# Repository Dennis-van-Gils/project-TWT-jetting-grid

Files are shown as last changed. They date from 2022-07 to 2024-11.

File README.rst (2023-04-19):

*This repository involves the Jetting Grid of the Twente Water Tunnel (TWT) facility of the University of Twente, Physics of Fluids group.*

Introduction
============

The Jetting Grid is essentially a turbulence generator. It consists of a rectangular array of 112 individually computer-controlled water jets that are aligned streamwise to the measurement section of our 8 meter tall vertically recirculating water tunnel. Individual jets will turn on and off following predefined 'protocols' tailored to different turbulent statistics inside the measurement section. The protocols are based on 4-dimensional OpenSimplex
noise: a type of gradient noise that features temporal and spatial coherence.

..
  More details can be found in the Review of Scientific Instruments article found here.

In this repository you can find:

.. list-table::
  :widths: 50 50

  * - The electronic design diagram
    - `</docs/electronic_diagram.pdf>`_
  * - The electronics cabinet in 3D-CAD
    - `</Solidworks/_main_cabinet.pdf>`_
  * - The microcontroller C++ source code and firmware
    - `</src_mcu>`_
  * - The Python user control program
    - `</src_python>`_
  * - The protocol generator based on 4D-OpenSimplex noise
    - `</protocols>`_
  * - Project photos
    - `</docs/photos>`_

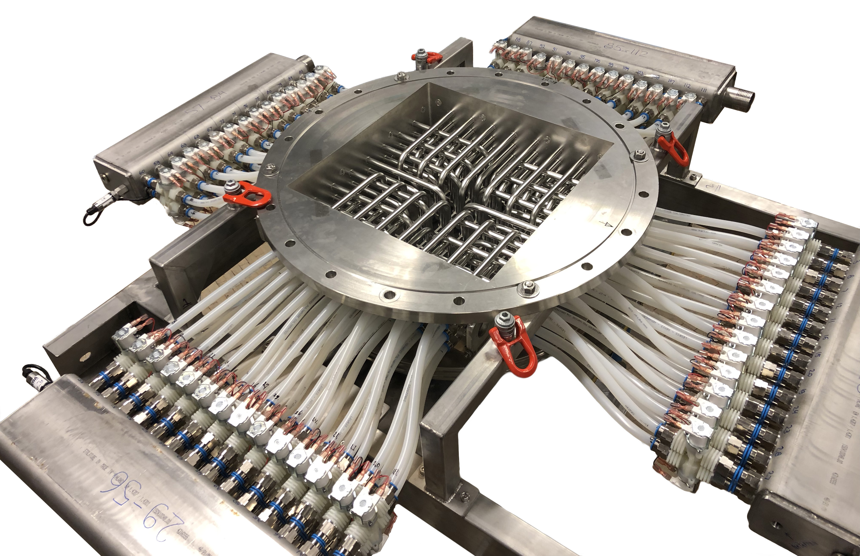
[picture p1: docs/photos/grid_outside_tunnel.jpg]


  *Figure 1: The jetting grid before installation in the tunnel.*

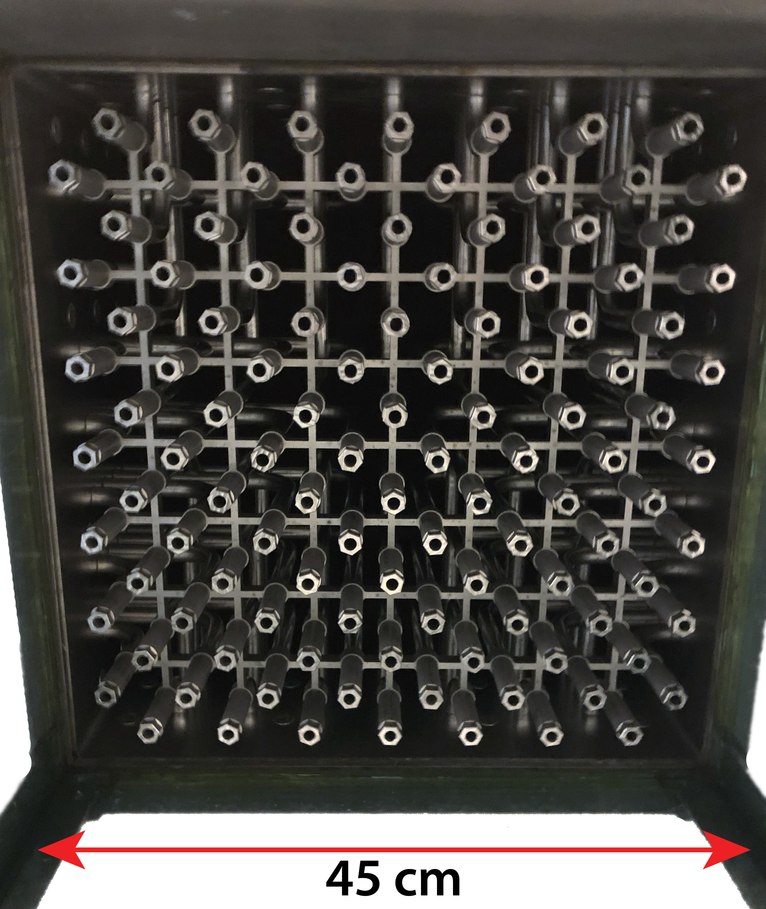
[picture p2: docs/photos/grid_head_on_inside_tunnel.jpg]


  *Figure 2: The jetting grid inside of the tunnel viewed head-on through the measurement section of cross-section 0.45 m by 0.45 m.*

Extended introduction
=====================

All jetting nozzles are powered by a single water pump providing the driving pressure for the jets. Each nozzle is controlled by an individual solenoid valve that can be programmatically opened or closed. The valves of the grid come in through the 4 side walls of the tunnel section with 28 valves through each side: 4 x 28 = 112 valves. Each set of these 28 valves shares a common pressure distribution manifold of which we will monitor the pressure.

An Arduino controls the 112 solenoid valves, reads out the 4 pressure sensors and drives a 16x16 LED matrix to visualize the status of each valve.

Protocol coordinate system (PCS)
================================

The jetting nozzles are laid out in a square grid, aka the protocol coordinate system (PCS): ::

      ●: Indicates a valve & nozzle
      -: Indicates no nozzle & valve exists

         -7 -6 -5 -4 -3 -2 -1  0  1  2  3  4  5  6  7
        ┌─────────────────────────────────────────────┐
      7 │ -  ●  -  ●  -  ●  -  ●  -  ●  -  ●  -  ●  - │
      6 │ ●  -  ●  -  ●  -  ●  -  ●  -  ●  -  ●  -  ● │
      5 │ -  ●  -  ●  -  ●  -  ●  -  ●  -  ●  -  ●  - │
      4 │ ●  -  ●  -  ●  -  ●  -  ●  -  ●  -  ●  -  ● │
      3 │ -  ●  -  ●  -  ●  -  ●  -  ●  -  ●  -  ●  - │
      2 │ ●  -  ●  -  ●  -  ●  -  ●  -  ●  -  ●  -  ● │
      1 │ -  ●  -  ●  -  ●  -  ●  -  ●  -  ●  -  ●  - │
      0 │ ●  -  ●  -  ●  -  ●  -  ●  -  ●  -  ●  -  ● │
     -1 │ -  ●  -  ●  -  ●  -  ●  -  ●  -  ●  -  ●  - │
     -2 │ ●  -  ●  -  ●  -  ●  -  ●  -  ●  -  ●  -  ● │
     -3 │ -  ●  -  ●  -  ●  -  ●  -  ●  -  ●  -  ●  - │
     -4 │ ●  -  ●  -  ●  -  ●  -  ●  -  ●  -  ●  -  ● │
     -5 │ -  ●  -  ●  -  ●  -  ●  -  ●  -  ●  -  ●  - │
     -6 │ ●  -  ●  -  ●  -  ●  -  ●  -  ●  -  ●  -  ● │
     -7 │ -  ●  -  ●  -  ●  -  ●  -  ●  -  ●  -  ●  - │
        └─────────────────────────────────────────────┘

The PCS spans ``(-7, -7)`` to ``(7, 7)`` where ``(0, 0)`` is the center of the grid. Physical valves are numbered 1 to 112, see `/docs/jetting_grid_indices.pdf </docs/jetting_grid_indices.pdf>`_.

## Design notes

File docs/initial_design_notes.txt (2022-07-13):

Solenoid water valve
--------------------

Number of valves:
Decided: 112, 28 per side, pref 12 mm inner diam

Typical 24V water solenoid valve draws 250 mA

Requirements solenoid valve:
- operate at 24 V (preferably: keep the current below 290 mA for the PVT312 solid state relay)
- diameter ~ 10 mm, 1/2", 3/8"
- fast acting ~ 0.5 to 1 sec
- direct or indirect (requires P_diff) controlled

Circuitry
---------

Use Arduino + Millipede board (MCP23017, 16 ch, I2C) + MOSFET board
Add a square matrix LED panel for jet visualisation.

Centipede: 64 channels extra DIO from I2C
Can probably take in 3.3 V I2C

  MOSFETS
  -------

Google: https://www.google.com/search?q=mosfet+board+16+channels&client=firefox-b-d&biw=1509&bih=934&sxsrf=AOaemvJO6wwmgFGnOk4NJ1rpOsNPfvxfmA:1638218075573&tbm=isch&source=iu&ictx=1&fir=AU-XXLih75zALM%252CS97yPO1Kx7uSEM%252C_%253B9pQUPeZW437mgM%252CEUD3R4LZVhkzxM%252C_%253Bhjt8wuJb8bHoEM%252CFV8Iuv8lZduGGM%252C_%253BljEDhoefagN5KM%252Cti9fFwPpx9osCM%252C_%253BCxuMXcBo8yG1DM%252CEUD3R4LZVhkzxM%252C_%253Be8bhNiFRVqvsCM%252CFV8Iuv8lZduGGM%252C_%253BFx3XZ33hJDuYoM%252CSX-uN8D8Pt4YaM%252C_%253BxeoLwY-jtr72NM%252CGLllsm-Hn3OM_M%252C_%253BPi-L7esW3UOClM%252CdukqlienmSXj_M%252C_%253B2DBUNCfDyTJj9M%252CGLllsm-Hn3OM_M%252C_&vet=1&usg=AI4_-kRFkAliVR6oQi8AF89qi7QxvJARFg&sa=X&ved=2ahUKEwioxNXztb70AhXdh_0HHbOiAd8Q9QF6BAgDEAE#imgrc=TQaBvuL1G480wM
  
Perhaps go with mosfets instead of solid state relays.
background: https://www.omron-ap.com/service_support/FAQ/FAQ02243/index.asp
not sold anymore: https://nl.aliexpress.com/item/295106416.html
good, but discontinued https://www.seeedstudio.com/16-Ch-High-Current-Driver-Shield-Kit-v2-p-793.html

Candidates MOSFET boards:
  1)  http://www.icstation.com/channel-amplifier-module-isolated-transistor-controller-signal-converter-16bit-protector-optocoupler-p-14065.html
      https://www.joom.com/en/products/5ee21e888b45130101fa9668
      https://nl.aliexpress.com/item/32802013615.html?spm=a2g0o.productlist.0.0.1ad72fd72K1Lzm&algo_pvid=5d4b663b-750f-42e6-8c23-180898b16d44&algo_exp_id=5d4b663b-750f-42e6-8c23-180898b16d44-46&pdp_ext_f=%7B%22sku_id%22%3A%2264206637981%22%7D
      
      Brand: Sanwo
      specs: optocoupled, < 1 ms response, 1 kHz switching freq, with LED indicators
             NPN in, NPN out
      eur 32

  2)  https://de.aliexpress.com/item/33014054266.html
      http://en.ginri.com/products-id60.html
      https://nl.aliexpress.com/item/32838587215.html?spm=a2g0o.productlist.0.0.21df7e0bMamRsn&algo_pvid=8064bbcf-e388-47e7-9a27-8b6d5d5a820e&algo_exp_id=8064bbcf-e388-47e7-9a27-8b6d5d5a820e-31&pdp_ext_f=%7B%22sku_id%22%3A%2265134071861%22%7D
      
      Brand: Ginri
      specs: > 5 kHz switching
             NPN or PNP in, PNP out
      eur 46.12

Design
------
Add master mechanical relay to control ENA_relays?
Decision: No. Relays should stay powered as they are to prevent
waterhammer when they would otherwise all close simultaneously in case
of EM stop or MCU restart.

Pumps
-----
Looking for 3-5 bar and 350l/min.

Flow meter ?
---------------
Before intake of pump
Decision: no, we only rely on pressure

Pressure sensor?
-----------------
Perhaps 1 on each manifold?
Decision: yes
Put manual restriction valve before each manifold to tune equal pressure distribution

How many valves will be enabled simultaneously?
-----------------------------------------------
If we choose to open all 112 valves it will draw 112 * 0.265 A = 30 A.
And the power draw will be 30 A * 24 V = 720 W.
This is fairly large. Not impossible, but I have to design for this.

Decision: Design for all valves open simultaneously at once, during measurement just 30

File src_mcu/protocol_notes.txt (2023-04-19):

Protocol file format:
    - Plain ASCII, tab delimited, rows ending with '\n' , not '\n\r'
    - Assume each row all valves are turned off, unless listed 

    [HEADER]
    ... (info to be able to generate the protocol)
    [DATA]
    [duration in ms, max 2^16-1] [list of open valves in grid (-7,-7) to (7,7)]
    50       -7,-2    3,2    1,2    4,-2
    50       -6,-4    3,6    -3,2
    100      ..... 

Memory allocation @ Arduino:

    Protocol:

    Send from Python to Arduino via binary serial stream
    ----------------------------------------------------
    Sends a single protocol line each time as follows:
      1x2 bytes: Duration in ms, big-endian
      Nx1 bytes: Each PCS point (x, y) packed into a single byte.
                 Upper 4 bits = PCS.x, lower 4 bits = PCS.y
      1x3 bytes: End-of-line (EOL) sentinel: [0xFF, 0xFF, 0xFF]

    When received at Arduino side
    -----------------------------
    Each line gets transformed into a 16x16 boolean matrix where all send PCS
    coordinates are 1's, the rest 0.
    Next, we pack each row of the matrix into a 16 bit structure, i.e. uint16_t.
    We have 15 rows of each 16 bits --> 30 bytes for the full boolean matrix
    +2 bytes for the time duration in ms as uint16_t
    ----> 30 + 2 = 32 bytes per protocol line, fixed number of bytes, regardless
    of how many valves should be opened or closed.
    This allows us to define a fixed-size array within C++, yeay!
    Say we have 180.000 bytes of RAM left over to play with:
    --> 180000/32 = 5625 protocol lines will fit into memory.
    Hence, we safely limit the max number of lines a protocol can contain to
    5000.

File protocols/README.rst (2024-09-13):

Protocols
=========

Contains the Python scripts to generate protocols for the jetting grid of the
Twente Water Tunnel facility.

Installation
------------

1) Download the contents of this GitHub folder `here <https://download-directory.github.io/?url=https%3A%2F%2Fgithub.com%2FDennis-van-Gils%2Fproject-TWT-jetting-grid%2Ftree%2Fmain%2Fprotocols>`_ and unzip.
2) Open Anaconda prompt and navigate into the unzipped folder.
3) Now, we will create a separate Python environment called 'twt' to install the necessary packages and run the scripts in.

    In Anaconda prompt::

        conda create -n twt python=3.10
        conda activate twt
        pip install -r requirements.txt

Usage
-----

* Edit ``config_proto_opensimplex.py`` to your needs.
* Set global flags in ``make_proto_opensimplex.py`` to your needs.

In Anaconda prompt::

    conda activate twt
    ipython make_proto_opensimplex.py

Example output
--------------

See the `protocols subfolder </protocols/protocols>`_.


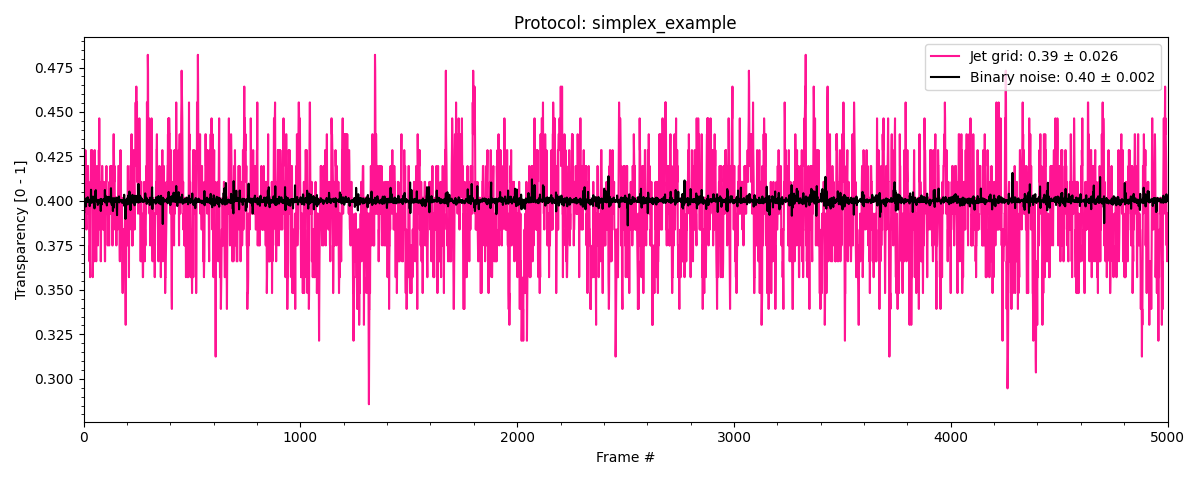
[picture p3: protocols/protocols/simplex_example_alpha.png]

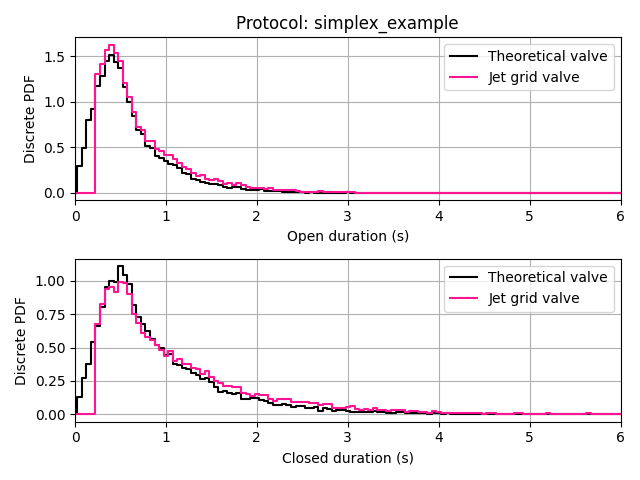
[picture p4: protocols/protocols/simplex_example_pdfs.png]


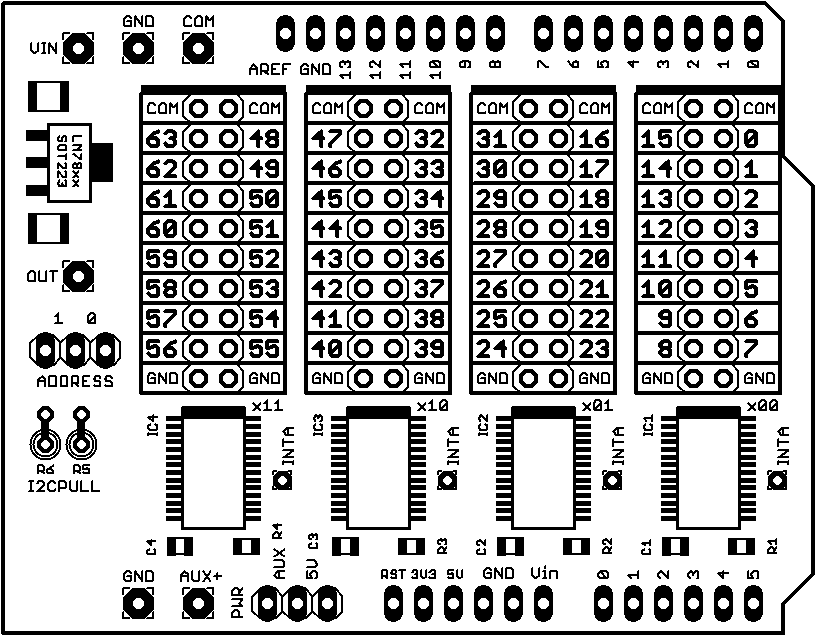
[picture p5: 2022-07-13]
docs/electronics/io_expander_centipede/photos/centipede_bitmap.png

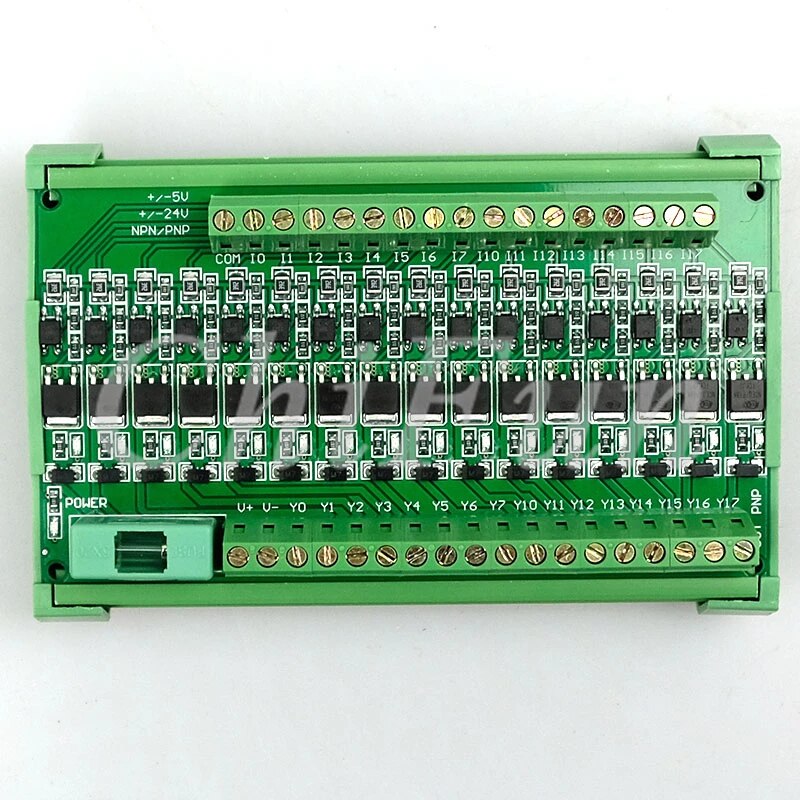
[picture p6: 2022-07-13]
docs/electronics/mosfet_board/photos/16-manier-PLC-versterkerprint-isolatie-boord-bescherming-boord-ingang-NPN-PNP-uitgang-PNP.jpg_Q90.jpg_.jpg

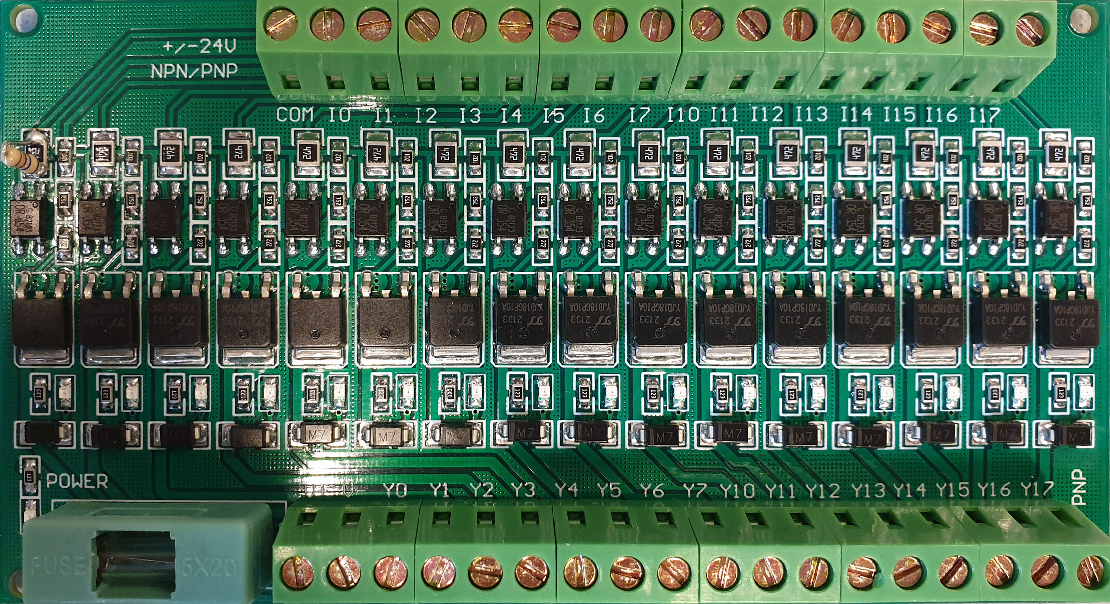
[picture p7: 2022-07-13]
docs/electronics/mosfet_board/photos/Sanwo_mosfet_board.jpg

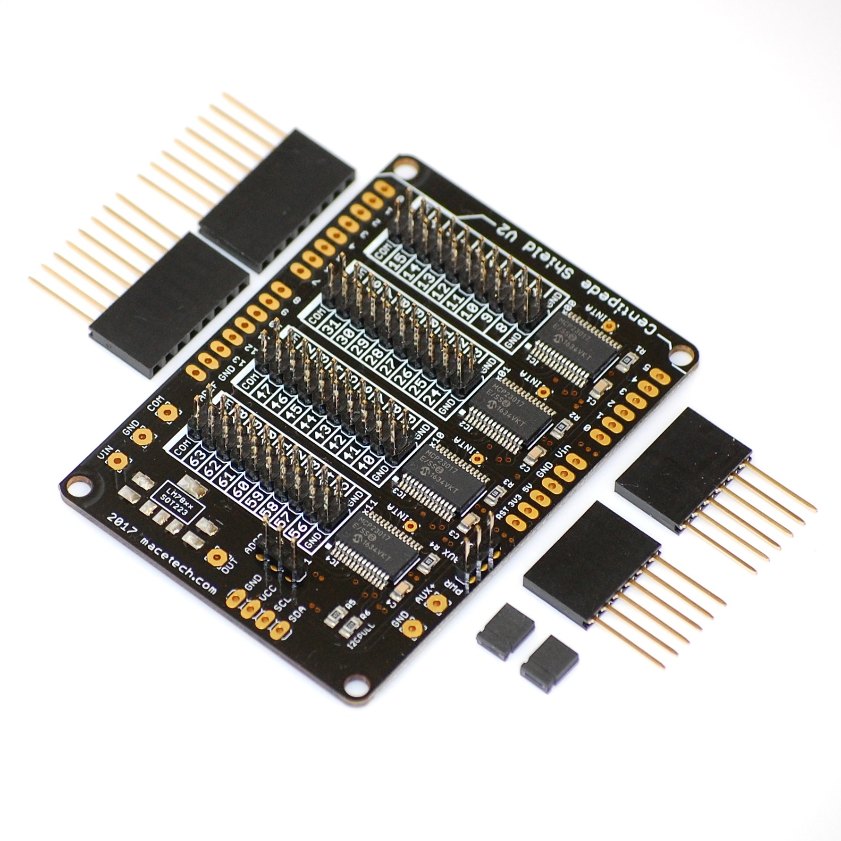
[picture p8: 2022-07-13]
docs/electronics/io_expander_centipede/photos/2019-11-24T07 14 23.657Z-DSC_6497.JPG

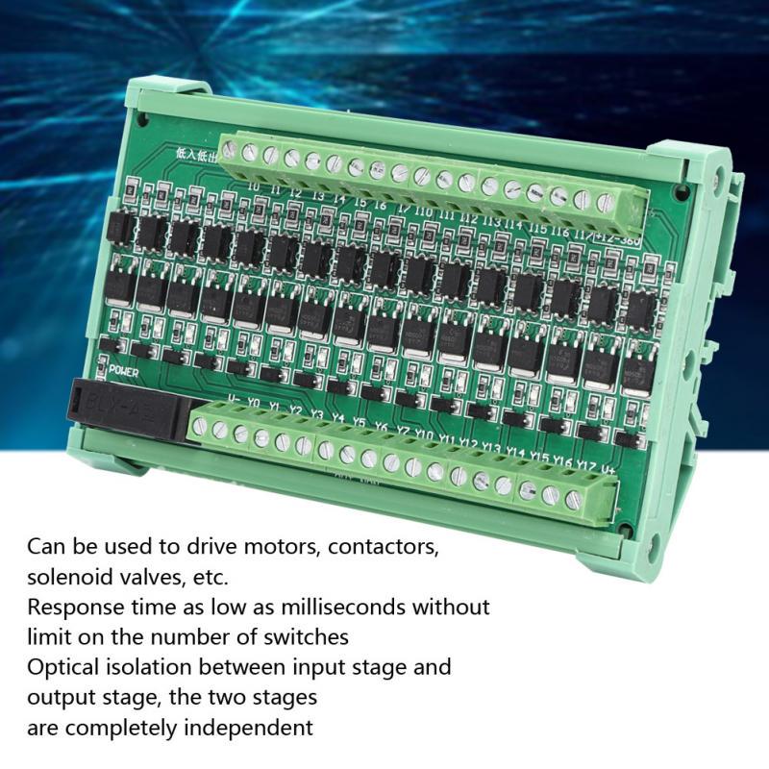
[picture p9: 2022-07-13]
docs/electronics/mosfet_board/photos/Sanwo.jpeg

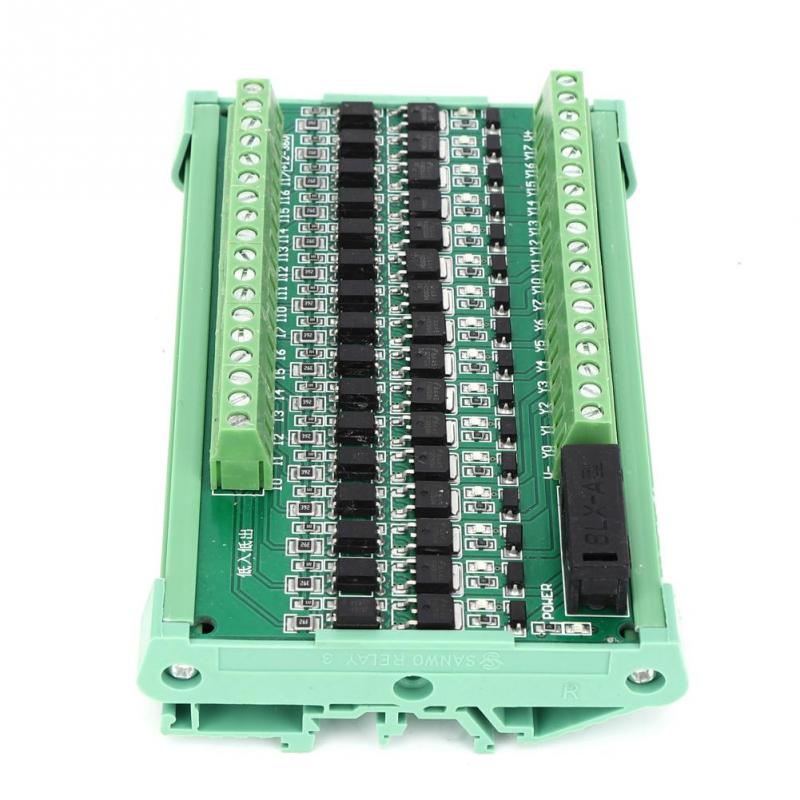
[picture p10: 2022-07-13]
docs/electronics/mosfet_board/photos/6e6c67497c9603db31151731857741b0994e5a79_original.jpeg

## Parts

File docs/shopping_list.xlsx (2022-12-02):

OFI: 30912301, PROJECT: 20001599-10
 | Delivered? | Item | Brand & type | Price per unit | Count | Total price | Link | Specs
Valves | yes | solenoid valves | RPE 5105NC-24VDC | €16.19 | 140 | €2266.60 | https://tameson.nl/kleppen/magneetventiel/2-weg/plastic/5105nc-24vdc-magneetventiel-2weg-012inch-nylon-0p2-10bar-nbr.html | 24 V, 265 mA
Main electronics | yes | Adafruit Feather M4 Express | Adafruit #3857 | €27.50 | 1 | €27.50 | https://www.kiwi-electronics.nl/en/adafruit-feather-m4-express-featuring-atsamd51-3578
 | yes | I2C I/O expander, 64 ch. | Macetech Centipede V2 | €25.00 | 2 | €50.00 | https://shop.macetech.com/products/centipede-shield-v2
 | yes | mosfet board, opto-coupled, 16 ch. | Aliexpress, Sanwo? | €22.22 | 8 | €177.76 | https://nl.aliexpress.com/item/32802013615.html
 | yes | pressure transducer | Omega PXM309-007GI | €137.00 | 4 | €548.00 | https://www.omega.nl/pptst/PXM309.html | G 1/4 (1/4" BSPP)
 | yes | pressure snubber | Omega PS-4E-MG | €14.50 | 4 | €58.00 | https://www.omega.nl/pptst/PS_SNUBBERS.html | G 1/4
 | yes | 4-20 mA receiver | MIKROE-1387 | €20.21 | 4 | €80.84 | https://nl.rs-online.com/web/p/products/8828948/
 | yes | PSU, 24 V, 31 A, 750 W | TRACO POWER TXLN 750-124 | €274.00 | 1 | €274.00 | https://nl.farnell.com/traco-power/txln-750-124/power-supply-ac-dc-24v-31-3a/dp/3647863 | For solenoid valves
 | yes | PSU din rail, 3.3 V, 2.6 A, 8.6 W | CUI PSK-10D-3-DIN | €15.00 | 1 | €15.00 | https://nl.farnell.com/cui/psk-10d-3-din/power-supply-ac-dc-3-3v-1-515a/dp/3702409 | For Arduino
 | yes | PSU din rail, 5 V, 6 A, 30 W | XP POWER DNR30US05 | €33.00 | 1 | €33.00 | https://nl.farnell.com/xp-power/dnr30us05/psu-din-rail-30w-5v/dp/1372693 | For LED matrix
 | yes | LED matrix, NeoPixel 16x16 | Adafruit #2547 | €85.00 | 1 | €85.00 | https://www.digikey.nl/nl/products/detail/adafruit-industries-llc/2547/5777186
 | yes | USB-RS485 isolated adapter | Titan USB-COMi-Si-M | €94.00 | 1 | €94.00 | https://www.antratek.nl/usb-comi-si-m
Safety microcontroller | yes | Adafruit Feather M0 Basic Proto | Adafruit #2772 | €22.72 | 1 | €22.72 | https://nl.rs-online.com/web/p/microcontroller-development-tools/1245520
 | yes | FeatherWing Doubler | Adafruit #2890 | €8.55 | 1 | €8.55 | https://nl.rs-online.com/web/p/breadboards/1245499
 | yes | Non-latching relay for Adafruit Feather | Adafruit #2895 | €9.07 | 1 | €9.07 | https://nl.rs-online.com/web/p/power-motor-robotics-development-tools/1245530
Custom perfboard | yes | perfboard 160x100 mm (set of 4) | Tru Components T1906SA024 | €25.61 | 1 | €25.61 | https://www.conrad.nl/nl/p/tru-components-printplaat-epoxide-l-x-b-160-mm-x-100-mm-35-m-rastermaat-2-54-mm-inhoud-4-stuk-s-2137879.html
 | yes | PCB 160x100 carrier DIN rail | DamenCNC 2340 | €21.00 | 2 | €42.00 | https://www.damencnc.com/en/din-rail-mount-for-eurocard-pcb-100x160mm/a1562
 |  | ↳ cheaper (next time) | Aliexpress |  |  |  | https://nl.aliexpress.com/item/32626843415.html
 | yes | screw terminals 4x, 2.54 pitch | Multicomp MP008515 | €0.82 | 20 | €16.40 | https://nl.farnell.com/multicomp-pro/mp008515/tb-wire-to-brd-r-a-4way-18awg/dp/3817462
 | yes | headers, 1x8 stacking | Multicomp 2212S-08SG-85 | €0.12 | 30 | €3.60 | https://nl.farnell.com/multicomp/2212s-08sg-85/socket-pcb-1-row-8way/dp/1593463
 | yes | DIP socket, 2x7 | Multicomp 2227MC-14-03-10-F1 | €0.22 | 10 | €2.20 | https://nl.farnell.com/multicomp/2227mc-14-03-10-f1/socket-ic-dil-0-3-14way/dp/1103845
Cables & connectors | yes | Han-ECO bulkhead housing | Harting 19 41 024 0301 | €14.00 | 8 | €112.00 | https://nl.farnell.com/harting/19-41-024-0301/housing-bulkhead-han-eco-24b/dp/1892252
 | yes | Han-ECO hood, M40 gland | Harting 19 41 124 0523 | €35.00 | 8 | €280.00 | https://nl.farnell.com/harting/19-41-124-0523/hood-s-e-m40-han-eco-24b-with/dp/1892257
 | yes | Han E screw module F | Harting 09 14 005 2701 | €7.40 | 56 | €414.40 | https://nl.farnell.com/harting/09-14-005-2701/rectangular-insert-signal-rcpt/dp/2382689
 | yes | Han E screw module M | Harting 09 14 005 2601 | €10.70 | 56 | €599.20 | https://nl.farnell.com/harting/09-14-005-2601/rectangular-insert-signal-plug/dp/2382688
 | yes | cable 35 x 0.5 mm2, per 50 meter | ÖLFLEX CLASSIC 110, 1119035 | €243.80 | 1 | €243.80 | https://www.conrad.nl/p/lapp-olflex-classic-110-stuurstroomkabel-35-g-050-mm-grijs-1119035-50-50-m-1029944 | OD 14.5 mm
 | yes | USB panel mount | TRU COMPONENTS USB-08 1243946 | €15.00 | 1 | €15.00 | https://www.conrad.nl/p/usb-inbouwbus-30-usb-08-1243946-tru-components-1-stuks-1243946
 | yes | ribbon cable, 2x10 header, 60 cm | Amphenol FC20600-0 | €2.34 | 10 | €23.40 | https://nl.farnell.com/amphenol/fc20600-0/lead-2-54mm-f-f-600mm-20way/dp/2217640
 | yes | ribbon cable, 20 way, 24 AWG, 25 m | Pro power PP001506 | €49.14 | 1 | €49.14 | https://nl.farnell.com/pro-power/pp001506/ribbon-cable-20core-24awg-300v/dp/2776631
 | yes | LED matrix: Shielded cable, plug | Phoenix 1424107 | €82.12 | 1 | €82.12 | https://nl.farnell.com/phoenix-contact/sac-4p-m12mss-10-0-pur-pe-sh/sensor-cord-4p-m12-plug-free-end/dp/3251948
 | yes | LED matrix: Panel mount, socket | Phoenix 1424137 | €16.25 | 1 | €16.25 | https://nl.farnell.com/phoenix-contact/sacc-e-m12fss-4con-m16-0-5-pe/sensor-lead-m12-socket-4pos/dp/2449288
 | yes | LED matrix: Panel mount EMC nut | Phoenix 1440164 | €1.27 | 2 | €2.54 | https://nl.farnell.com/phoenix-contact/1440164/emc-nut-size-m16-m12-connector/dp/2545245
 | ordered | LED matrix: Cable connector, socket | Phoenix 1404642 | €20.63 | 1 | €20.63 | https://nl.farnell.com/phoenix-contact/sacc-m12fss-3pecon-pg11-m/sensor-actuator-socket-m12-4pos/dp/2449313
 | yes | LED matrix: Panel mount, plug | Phoenix 1424139 | €16.70 | 1 | €16.70 | https://nl.farnell.com/phoenix-contact/sacc-e-m12mss-4con-m16-0-5-pe/sensor-lead-m12-plug-4pos/dp/2449272
 | yes | power dist. blocks: PTFIX 6/6X2,5 RD | Phoenix 3273334 | €2.59 | 10 | €25.90 | https://nl.farnell.com/phoenix-contact/ptfix-6-6x2-5-rd/tb-power-distribution-7pole-12/dp/2850258
 | yes | power dist. blocks: PTFIX 6/6X2,5 BK | Phoenix 3273344 | €2.60 | 10 | €26.00 | https://nl.farnell.com/phoenix-contact/ptfix-6-6x2-5-bk/tb-power-distribution-7pole-12/dp/2850263
 | yes | power dist. blocks: PTFIX 6/6X2,5 BU | Phoenix 3273332 | €2.60 | 10 | €26.00 | https://nl.farnell.com/phoenix-contact/ptfix-6-6x2-5-bu/tb-power-distribution-7pole-12/dp/2850257
 | yes | power dist. blocks: PTFIX 6/6X2,5 BN | Phoenix 3273340 | €2.75 | 10 | €27.50 | https://nl.farnell.com/phoenix-contact/ptfix-6-6x2-5-bn/tb-power-distribution-7pole-12/dp/2850261
 | yes | power dist. blocks: clamps DIN35 | Phoenix 3274056 | €0.38 | 50 | €19.00 | https://nl.farnell.com/phoenix-contact/ptfix-ns35a/din-rail-adapter-terminal-block/dp/2850283
 | yes | Harting 230V, body | Harting 19200031440 | €7.62 | 1 | €7.62 | https://nl.farnell.com/harting/19200031440/hood-top-entry-size-3a-metal/dp/2101928
 | yes | Harting 230V, cable gland | Harting 19000005080 | €9.07 | 1 | €9.07 | https://nl.farnell.com/harting/19000005080/cable-clamp-m20-5-9mm/dp/1707713
 | yes | Harting 230V, male insert | Harting 09200032611 | €9.25 | 1 | €9.25 | https://nl.farnell.com/harting/09200032611/rectangular-han-insert-plug-3way/dp/1178148
 | yes | Harting 230V, female insert | Harting 09200032711 | €14.17 | 1 | €14.17 | https://nl.farnell.com/harting/0920-003-2711/socket-han3a-3-e-way/dp/314717
 | yes | Harting 230V, bulkhead mount | Harting 09200030301 | €8.51 | 1 | €8.51 | https://nl.farnell.com/harting/0920-003-0301/housing-bulkhead-size-3a-1-lever/dp/314730
 | yes | Power switch, IP65 | Arcolectric c1353algnf | €6.41 | 1 | €6.41 | https://nl.farnell.com/arcolectric/c1353algnf/switch-dpst-red-i-o-16a-250v/dp/480368
 | yes | USB panel mount, IP65 | Bulgin PX0844/B/0M50/B | €15.47 | 1 | €15.47 | https://nl.farnell.com/bulgin/px0844-b-0m50-b/computer-cable-usb-2-0-0-5m-black/dp/2454629
 | yes | USB cable, IP65 | Bulgin px0840 b 5m00 | €28.96 | 1 | €28.96 | https://nl.farnell.com/bulgin/px0840-b-5m00/lead-usb-b-type-5m-ip68/dp/9997407
 | yes | Cable glands, M20x1.5 | Jacob 50013M20PASW-F | €0.60 | 30 | €18.00 | https://nl.farnell.com/jacob/50013m20pasw-f/gland-dome-top-polyamide-m20/dp/1168784
 | yes | Cable shoes, crimp, quick disconnect terminal | AMP 518553-000 | €0.80 | 300 | €240.00 | https://nl.farnell.com/amp-te-connectivity/518553-000/contact-socket-18-15awg/dp/1863417
 | yes | Cable 22 AWG, red, stranded, tinned, PVC | Alpha wire 3051 RD005, 30m | €13.57 | 2 | €27.14 | https://nl.farnell.com/alpha-wire/3051-rd005/wire-red-22awg-7-30awg-30-5m/dp/2290861
 | yes | Cable 22 AWG, black, stranded, tinned, PVC | Alpha wire 3051 BK005, 30m | €14.68 | 2 | €29.36 | https://nl.farnell.com/alpha-wire/3051-bk005/wire-blk-22awg-7-30awg-30-5m/dp/2290872
 | yes | DB9 panel mount connector, male | Multicomp Pro MC000958 | €6.12 | 1 | €6.12 | https://nl.farnell.com/multicomp/mc000958/connector-d-sub-plug-9pos-panel/dp/2473037
 | yes | DB9 panel mount connector, female | Multicomp Pro MC000961 | €7.29 | 1 | €7.29 | https://nl.farnell.com/multicomp/mc000961/connector-d-sub-rcpt-9pos-panel/dp/2473038
 | yes | DB9 cable connector, female | Multicomp Pro MC000969 | €7.73 | 1 | €7.73 | https://nl.farnell.com/multicomp/mc000969/conn-assembly-d-sub-rcpt-9pos/dp/2473043
 | yes | DB9 cable connector, male | Multicomp Pro MC000970 | €9.24 | 1 | €9.24 | https://nl.farnell.com/multicomp/mc000970/conn-assembly-d-sub-plug-9pos/dp/2473044
Enclosure | yes | Rittal cabinet, customized | Rittal 1076000 | €318.16 | 1 | €318.16 | Via webform
 | yes | cable tray 2000 x 25 x 80 | Hager HA78002 | €28.50 | 1 | €28.50 | https://www.conrad.nl/nl/p/hager-ha780025-kabelgoot-l-x-b-x-h-2000-x-25-x-80-mm-1-stuk-s-lichtgrijs-2249220.html
 | yes | DIN rail 35 mm, 2m | Multicomp Pro SPC10575 | €9.83 | 3 | €29.49 | https://nl.farnell.com/multicomp/spc10575/din-mounting-rail-2m-steel/dp/2395859

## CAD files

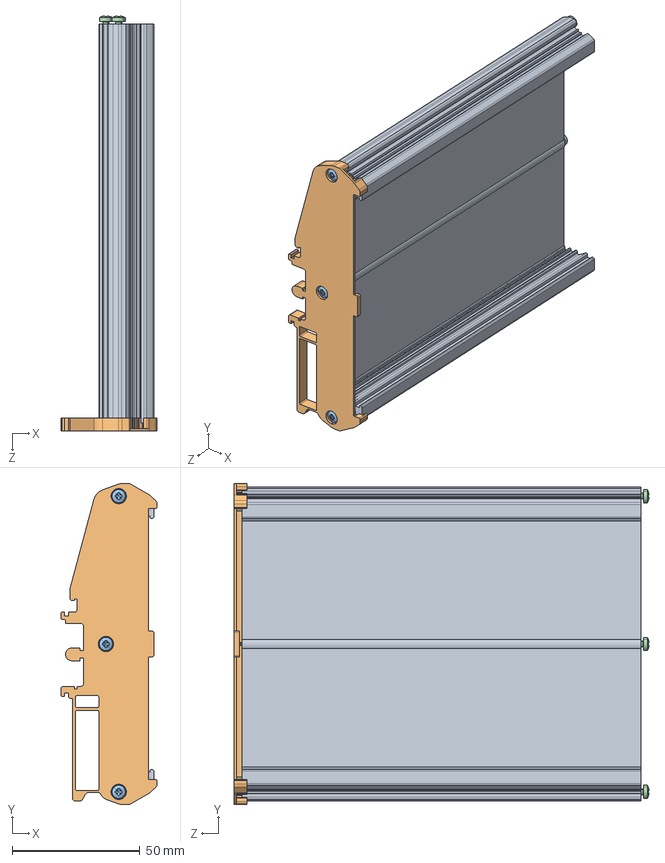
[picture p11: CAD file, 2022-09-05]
Solidworks/PCB_carrier/Damen_CNC_2340-1_DIN-Rail_Mount_for_Eurocard_PCB_100x160mm_STEP214.SLDASM
37.6 x 125.4 x 162.0 mm
eBom-prt0^2340-1_DIN-Rail_Mount_for_Eurocard_PCB_100x160mm_STEP214_Damen_CNC_2340-1_DIN-Rail_Mount_for_Eurocard_PCB_100x160mm_STEP214
eBom-prt1^2340-1_DIN-Rail_Mount_for_Eurocard_PCB_100x160mm_STEP214_Damen_CNC_2340-1_DIN-Rail_Mount_for_Eurocard_PCB_100x160mm_STEP214
eBom-prt2^2340-1_DIN-Rail_Mount_for_Eurocard_PCB_100x160mm_STEP214_Damen_CNC_2340-1_DIN-Rail_Mount_for_Eurocard_PCB_100x160mm_STEP214 x 3
eBom-prt4^2340-1_DIN-Rail_Mount_for_Eurocard_PCB_100x160mm_STEP214_Damen_CNC_2340-1_DIN-Rail_Mount_for_Eurocard_PCB_100x160mm_STEP214 x 3

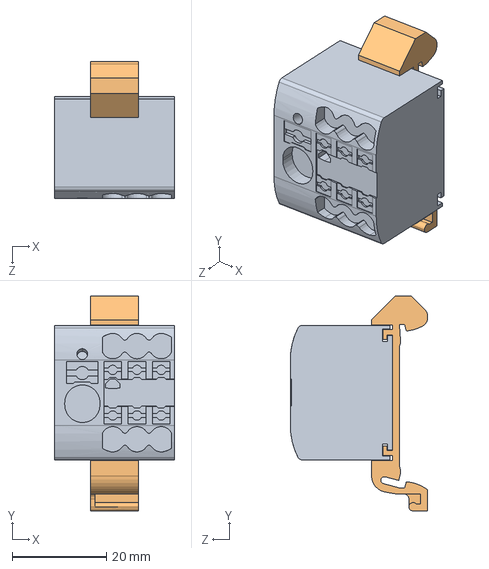
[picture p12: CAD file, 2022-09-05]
Solidworks/Phoenix_Contact/PTFIX_term_6-6X2,5 RD.SLDASM
25.6 x 45.7 x 29.2 mm
3273334_PTFIX_6_6x2.5_RD-select^3273334_PTFIX_6_6x2.5_RD-select_3273334

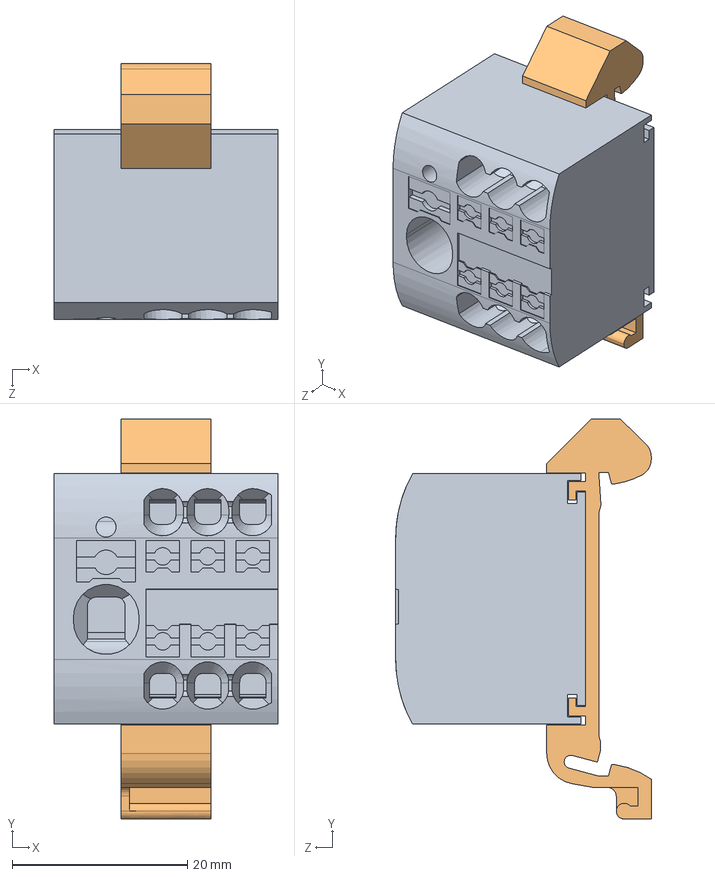
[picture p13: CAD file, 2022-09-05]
Solidworks/Phoenix_Contact/PTFIX_term_6-6X2,5 BK.SLDASM
25.6 x 45.7 x 29.2 mm
PTFIX_6_6X2.5_BK-select^3273344_03_PTFIX-6-6X2-5-BK_3D_3273344

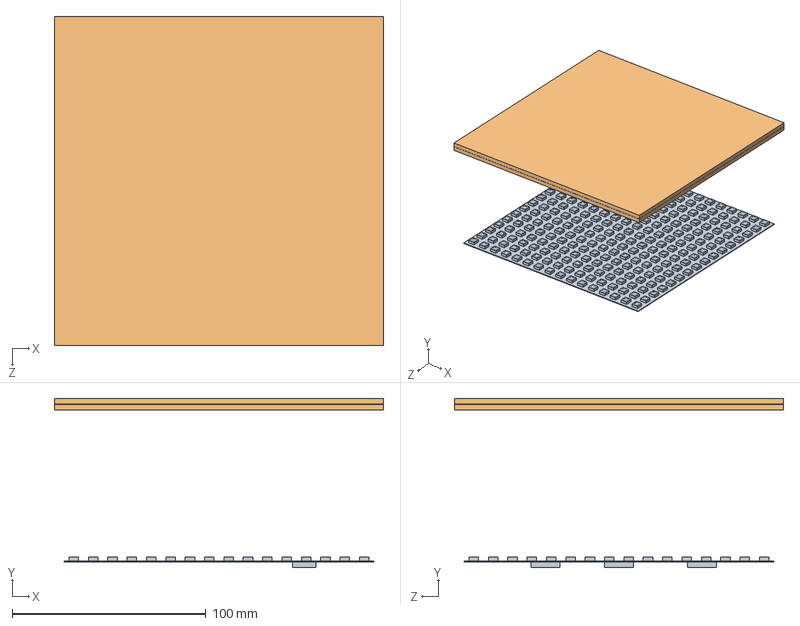
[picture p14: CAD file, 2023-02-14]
Solidworks/LED_matrix_backing_plate.SLDASM
170.0 x 87.5 x 170.0 mm
Adafruit_2547_flexible_16x16_NeoPixel_LED_matrix
LED_matrix_front_plate_1 x 2
LED_matrix_diffusor

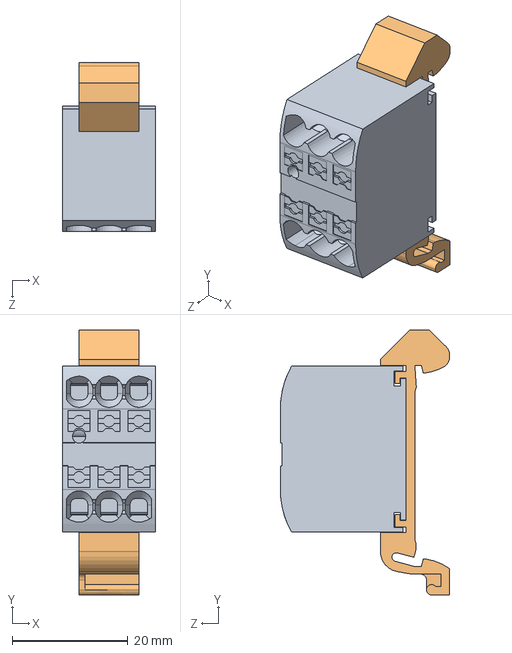
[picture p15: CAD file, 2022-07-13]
Solidworks/Phoenix_Contact/PTFIX_term_6X2,5 RD.SLDASM
16.0 x 45.7 x 29.2 mm

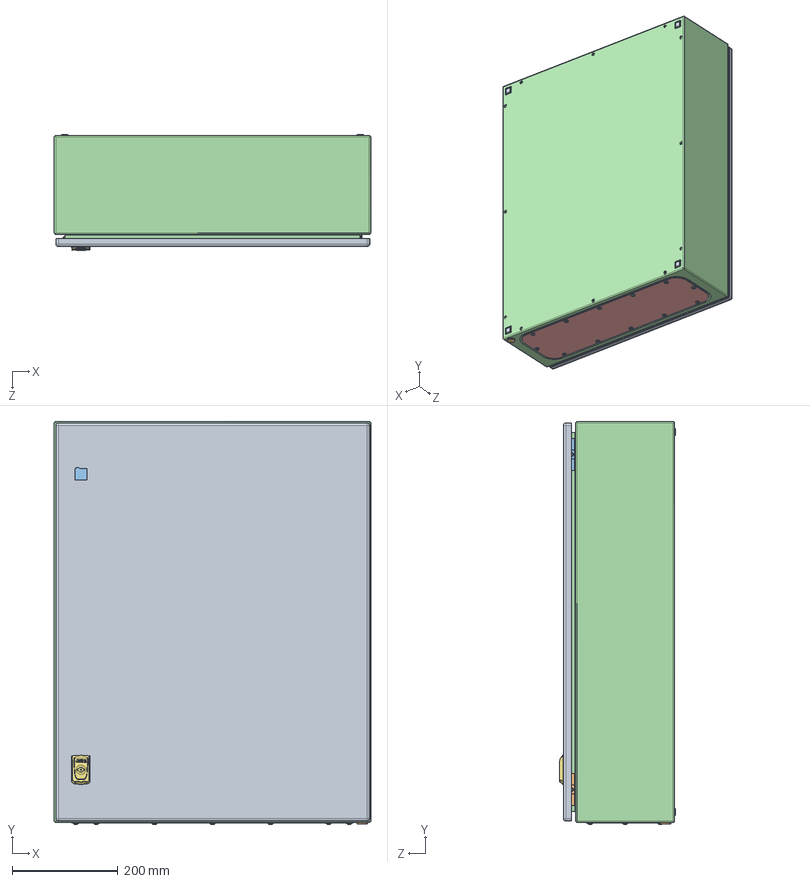
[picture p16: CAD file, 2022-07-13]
Solidworks/Rittal/1076_000_1_.sldasm
600.0 x 763.7 x 219.3 mm

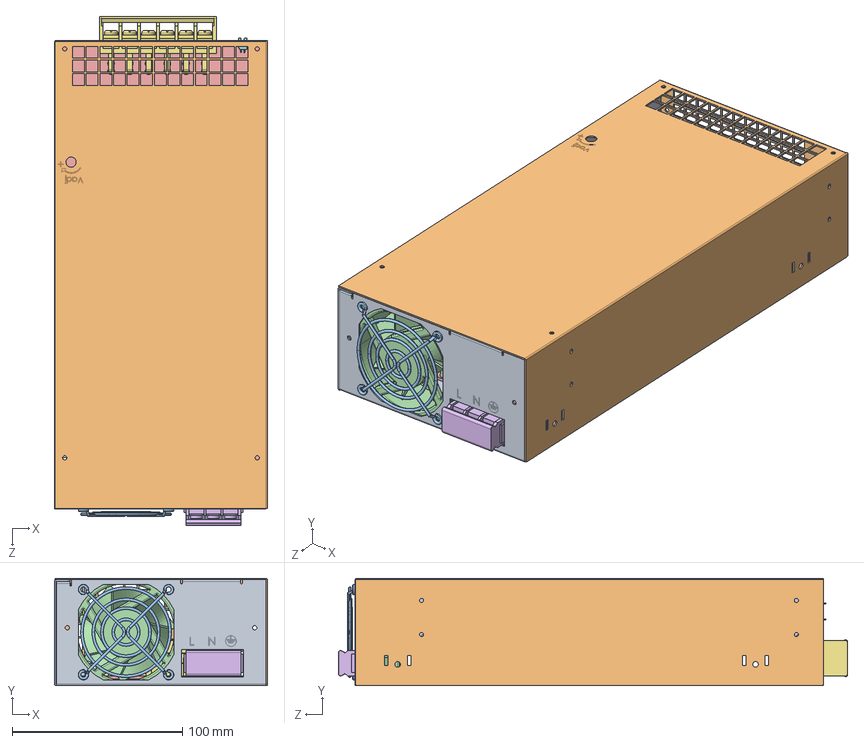
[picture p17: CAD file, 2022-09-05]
Solidworks/Traco_power/txln750_3D_drawing.stp.SLDASM
125.0 x 63.0 x 298.9 mm
CASE.stp
COVER.stp
FAN GUARD.stp
FAN60x25.stp
PCB.stp
TML BLK1.stp
TML BLK2.stp
HOUSING.stp

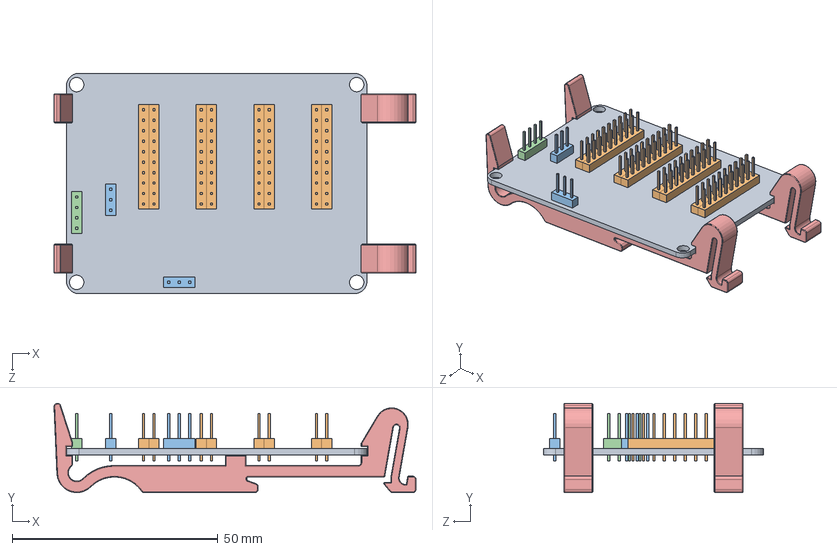
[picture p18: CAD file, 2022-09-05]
Solidworks/Centipede_shield_v2_with_clips.SLDASM
87.9 x 21.7 x 53.5 mm
Centipede_shield_v2
header_m2x10 x 4
header_m3 x 2
header_m4
DIN_rail_clip_73 x 2

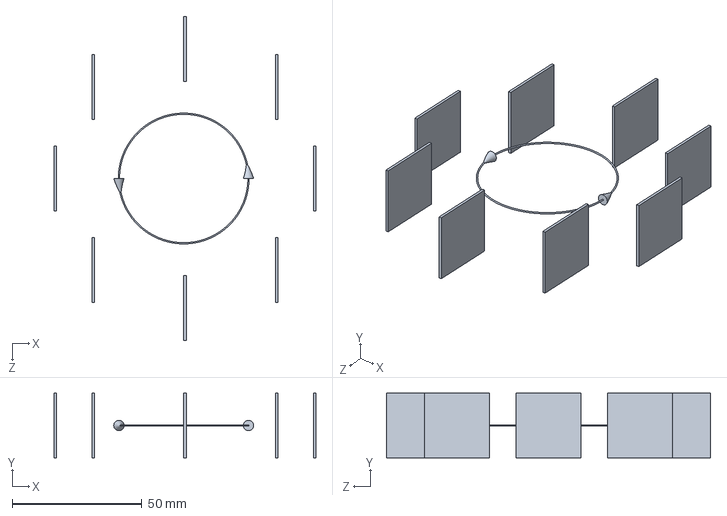
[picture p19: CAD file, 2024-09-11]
protocols/figures_for_publication/4D_noise_loop/4D_noise_loop.SLDPRT
101.0 x 25.0 x 125.0 mm

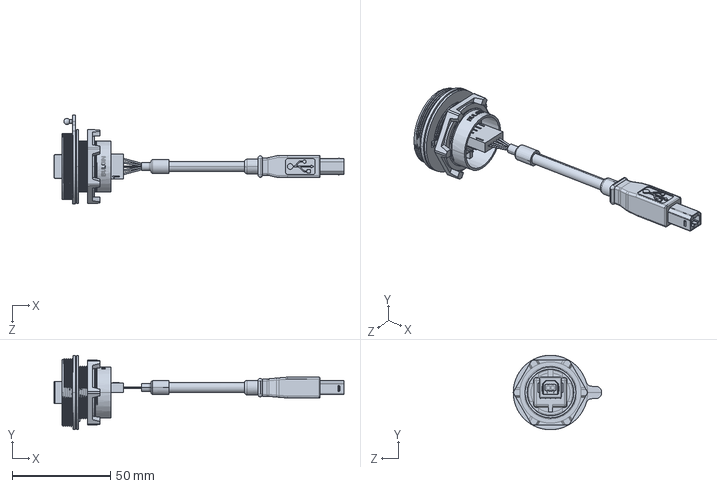
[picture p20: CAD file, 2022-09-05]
Solidworks/Bulgin/px0844-b-0m50-b.stp.SLDPRT
147.7 x 37.9 x 45.1 mm

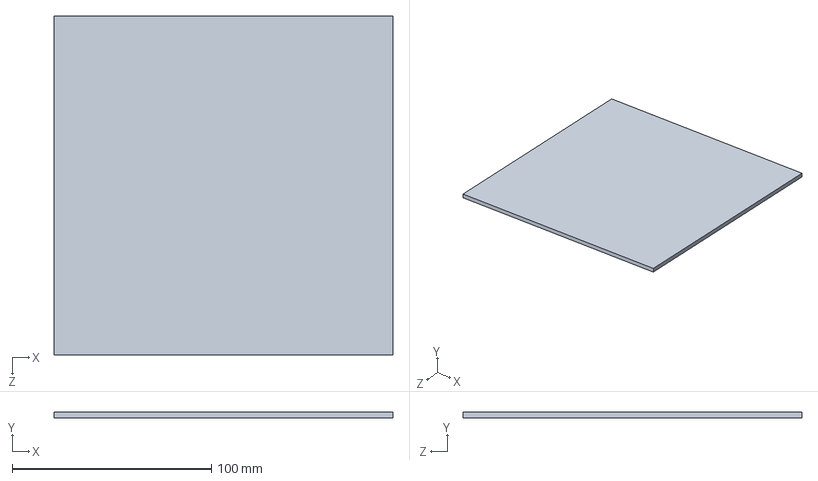
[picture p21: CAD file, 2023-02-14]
Solidworks/LED_matrix_front_plate_1.SLDPRT
170.0 x 3.00 x 170.0 mm

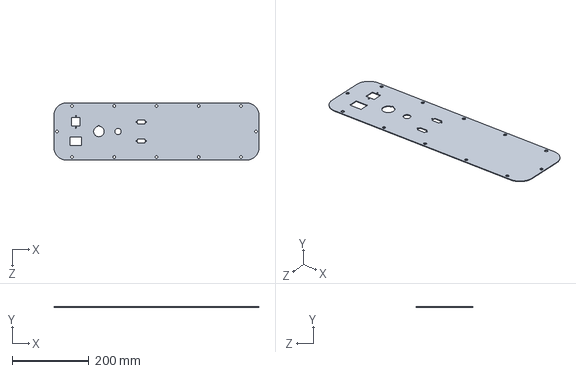
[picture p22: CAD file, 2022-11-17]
Solidworks/Rittal/1076_000_1__25_customized.SLDPRT
534.0 x 1.50 x 149.0 mm

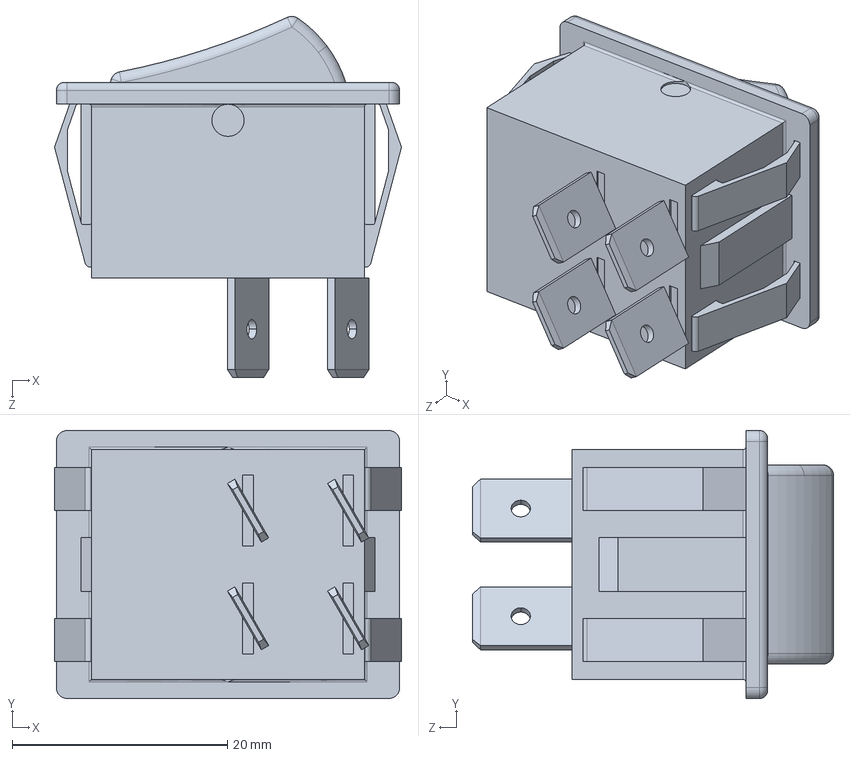
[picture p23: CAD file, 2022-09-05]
Solidworks/Bulgin/c1350al.stp.SLDPRT
32.2 x 24.9 x 33.6 mm

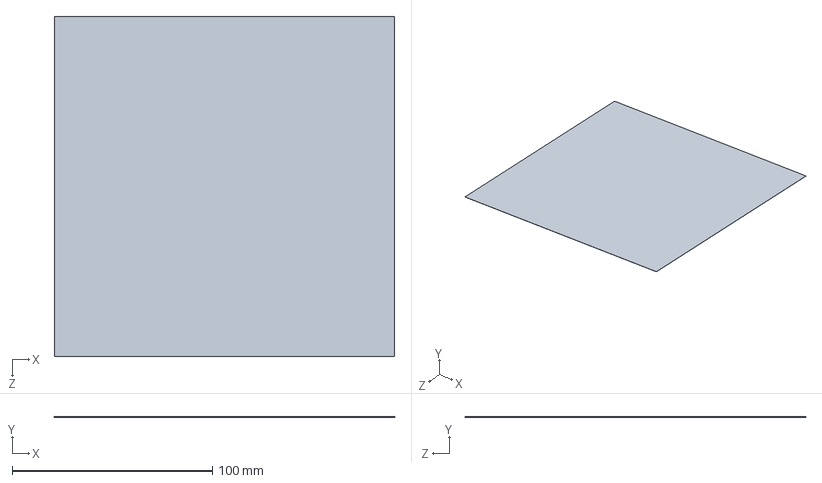
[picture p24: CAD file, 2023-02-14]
Solidworks/LED_matrix_diffusor.SLDPRT
170.0 x 0.1 x 170.0 mm

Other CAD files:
Solidworks/Rittal/1076_000_1_customized.SLDASM
Solidworks/Phoenix_Contact/PTFIX_term_6X2,5 BK.SLDASM
Solidworks/Traco_power/HOUSING.stp.SLDPRT
Solidworks/Traco_power/CASE.stp.SLDPRT
Solidworks/Adafruit_2547_flexible_16x16_NeoPixel_LED_matrix.SLDPRT
Solidworks/CUI_PSK-10D-3-DIN.sldprt
Solidworks/DIN_rail_35x7.5_long.SLDPRT
Solidworks/DIN_rail_35x7.5_psus.SLDPRT
Solidworks/DNR30_60.SLDPRT
Solidworks/LED_matrix_backing_plate.DXF
Solidworks/LED_matrix_backing_plate.SLDPRT
Solidworks/Phoenix_Contact/1424137.SLDPRT
Solidworks/Phoenix_Contact/3273268.SLDPRT
Solidworks/Phoenix_Contact/3273278.SLDPRT
Solidworks/Phoenix_Contact/3273334.SLDASM
Solidworks/Phoenix_Contact/3273344.SLDASM
Solidworks/Phoenix_Contact/3274056.SLDPRT
Solidworks/Phoenix_Contact/PTFIX_term_12X2,5 BK.SLDPRT
Solidworks/Rittal/1076_000_1__10.sldprt
Solidworks/Rittal/1076_000_1__12.sldprt
Solidworks/Rittal/1076_000_1__25.sldprt
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

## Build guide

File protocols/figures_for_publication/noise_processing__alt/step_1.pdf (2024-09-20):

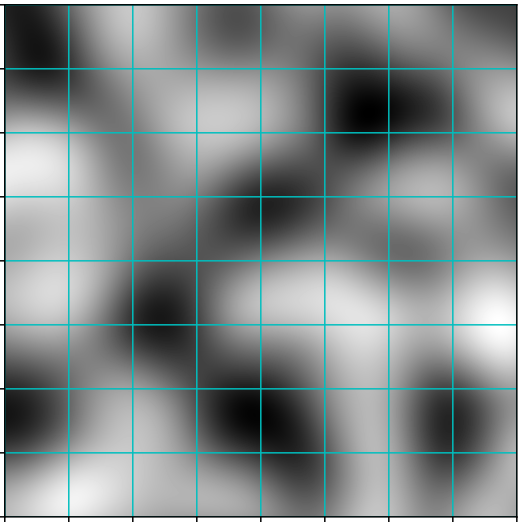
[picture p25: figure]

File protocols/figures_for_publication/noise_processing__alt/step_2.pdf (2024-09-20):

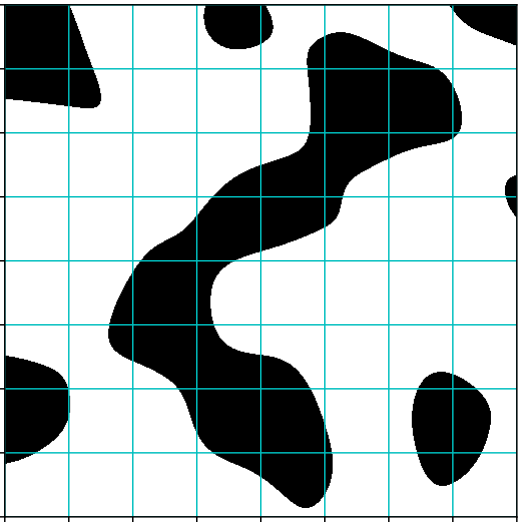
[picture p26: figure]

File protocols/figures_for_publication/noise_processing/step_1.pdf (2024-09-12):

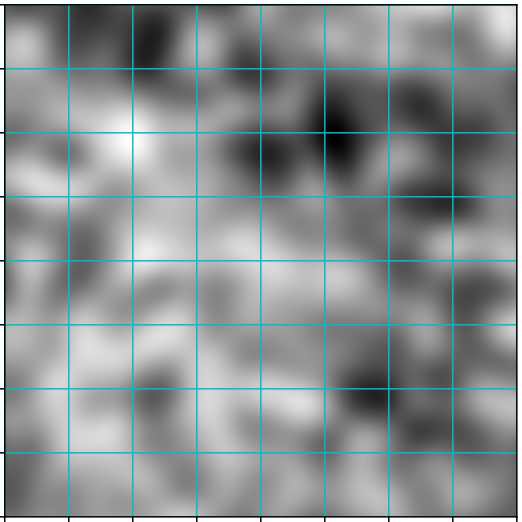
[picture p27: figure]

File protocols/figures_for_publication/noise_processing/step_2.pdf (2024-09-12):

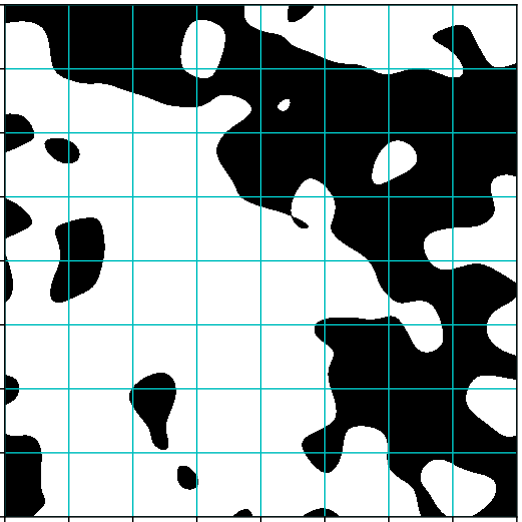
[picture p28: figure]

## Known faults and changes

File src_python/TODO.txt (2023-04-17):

* Implement shortcut keys for protocol step navigation:

A la code example:
"""
openFile = QAction(QIcon('open.png'), 'Open', self)
openFile.setShortcut('Ctrl+O')
openFile.setStatusTip('Open new File')
openFile.triggered.connect(self.showDialog)
"""

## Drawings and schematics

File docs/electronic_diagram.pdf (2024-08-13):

power switch

Arcolectric c1353algnf

USB isolator

Olimex USB-ISO

pressure manifold #2
(valves 29 to 56 & pressure sensor #2)

pressure manifold #3
(valves 57 to 84 & pressure sensor #3)

pressure manifold #2
(valves 85 to 112 & pressure sensor #4)

MCP23017

Arduino pass-through
(not connected)

Arduino pass-through
(not connected)
PWR
jumper

ADDRESS
jumper

I2C I/O expander, 64 ch.
Macetech Centipede V2
1 of 2

VSS

VDD

title : Electronic diagram `TWT jetting grid`
author : Dennis van Gils
url | : https://github.com/Dennis-van-Gils/project-TWT-jetting-grid
date | : 13-08-2024

I0

COM

Y0

V-V+

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
Shifun K Workshop
16 ch. MOSFET board
modified for 3.3V
1 of 8

fuse

24 VDC PSU
31 A, 750 W
TRACOPOWER
TXLN 750-124

3.3 VDC PSU
2.6 A, 8.6W
CUI
PSK-10D-3-DIN

Windows & Python

24 VDC

repeat for 14 channels ribbon cable 20 ways

Amphenol
FC20600-0

Purpose: Control 112 solenoid valves @ 24 V by a single Arduino. We will use two Centipede boards (only one shown), each providing 64 digital outputs controlled over I2C. Each Centipede board will have 4 MOSFET boards connected to them, each providing 16 channels. Hence, there is a total of 8 MOSFET boards to control in total 112 (max 128) solenoid valves. We will work in groups of 14, because 8x14=112. Also, each of the 4 sides of the tunnel will house 2x14=28 valves. Cable management is easier this way. Hence, instead of populating all 16 channels per MOSFET board, we occupy only the first 14.

draws 62 mA over 14 ch.

pressure sensor #1
Omega PXM309-007GI

4-20 mA

I0

COM

Y0

V-V+

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
Shifun K Workshop
16 ch. MOSFET board
modified for 3.3V
2 of 8

fuse

24 VDC

cable connector
Harting 19 41 124 0523
& 7x insert 09 14 005 2601 1 of 4
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
repeat for 14 channels repeat for 14 channels

N.C.
N.C.

N.C.
N.C.

N.C.
N.C.

N.C.
N.C.

repeat for 14 channels repeat for 14 channels draws 3.7 A over 14 solenoids

mA+
GND

CS
SDO
SCK

GND

### 3.3 V

GND

### 5 V

4-20mA R click

MIKROE-1387

### 1 of 4

read pressure 1 (4-20mA)

CS_pressure_1

active receiver
(provides 16 VDC)

MISO

CS_pressure_3

CS_pressure_4

CS_pressure_2

CS_pressure_1
35 x 0.5 mm², OD 14.5 mm
ÖLFLEX CLASSIC 110, 1119035

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
cable connector
Harting 19 41 124 0523
& 7x insert 09 14 005 2701

bulkhead connector
Harting 19 41 024 0301
& 7x insert 09 14 005 2701 1 of 4

bulkhead connector
Harting 19 41 024 0301
& 7x insert 09 14 005 2601

MS

motor
3ph 400 VAC, 10.5 A, 7.5 kW

Lowara PLM 132 B5 7.5 kW

jetting pump
6.8 kW, 2900 rpm, 60 m³/h

Xylem Lowara 46SVH2N075T/4

MODBUS RS485 (TxD+, TxD-, GND)

L1,L2,L3,PE

Rittal cabinet

wall power
230 VAC
USB B | USB A

USB B USB-RS485
opt. isolated

Titan USB-COMi-SI-M

USB B

µUSB

USB A | USB B

wall GND

draws
~ 4 A

“Main MCU”

Adafruit
Feather
M4 Express

Adafruit
#3857

!RESET
+3V3
AREF
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
MOSI
MISO
RX_D0
TX_D1
D4

VBAT
EN
VBUS
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
Rittal cabinet lab environment

pressure manifold #1

etc.

solenoid valve
RPE 5105NC-24VDC
24 V, 265 mA
1 of 28

water
pressure from
jetting pump

28x

pressure snubber
Omega PS-4E-MG

jetting
nozzle

GND

GND

valve #1

valve #1

28x

28x

connector
2 of 4

connector
3 of 4

connector
4 of 4

5 VDC PSU
6 A, 30 W
XP POWER
DNR30US05

GND

+5V

DATA

LED data (3.3V)

LED data (3.3V)

LED data (5V)

USB A

freq. inverter
3ph 400 VAC, Imax = 17 A
Xylem Hydrovar 4.075

u
wv
400 V
water pressure
from jetting pump

iso. GND

iso.
GND

3.3 VDC

GND

VCC

SCL

SDA

0
ADDR
1

AUX
PWR

GND

COM

GND

AUX+

INTA
MCP23017

INTA
MCP23017

INTA
MCP23017

INTA

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
2x10

max 125 mA
over 16 ch.

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
2x10

max 125 mA
over 16 ch.

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
2x10

max 125 mA
over 16 ch.

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
2x10

max 125 mA
over 16 ch.

AREF
GND
13

12

11

109876543210

RST

3V3
5V

GND

GND
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

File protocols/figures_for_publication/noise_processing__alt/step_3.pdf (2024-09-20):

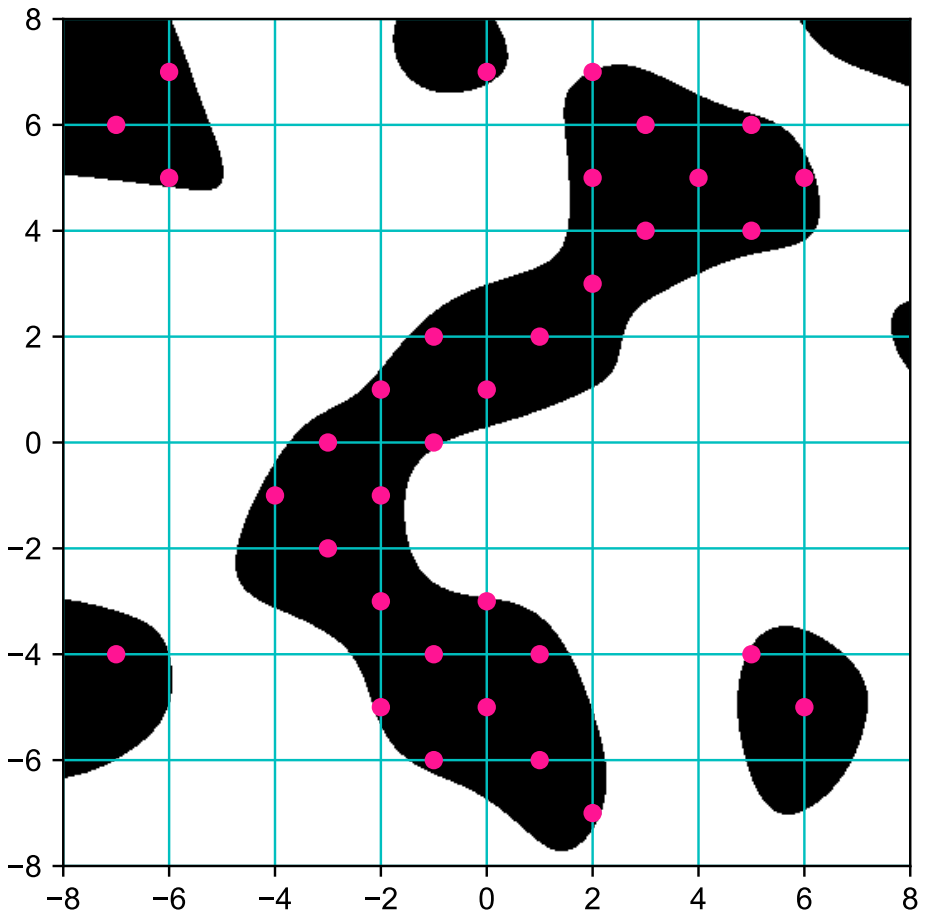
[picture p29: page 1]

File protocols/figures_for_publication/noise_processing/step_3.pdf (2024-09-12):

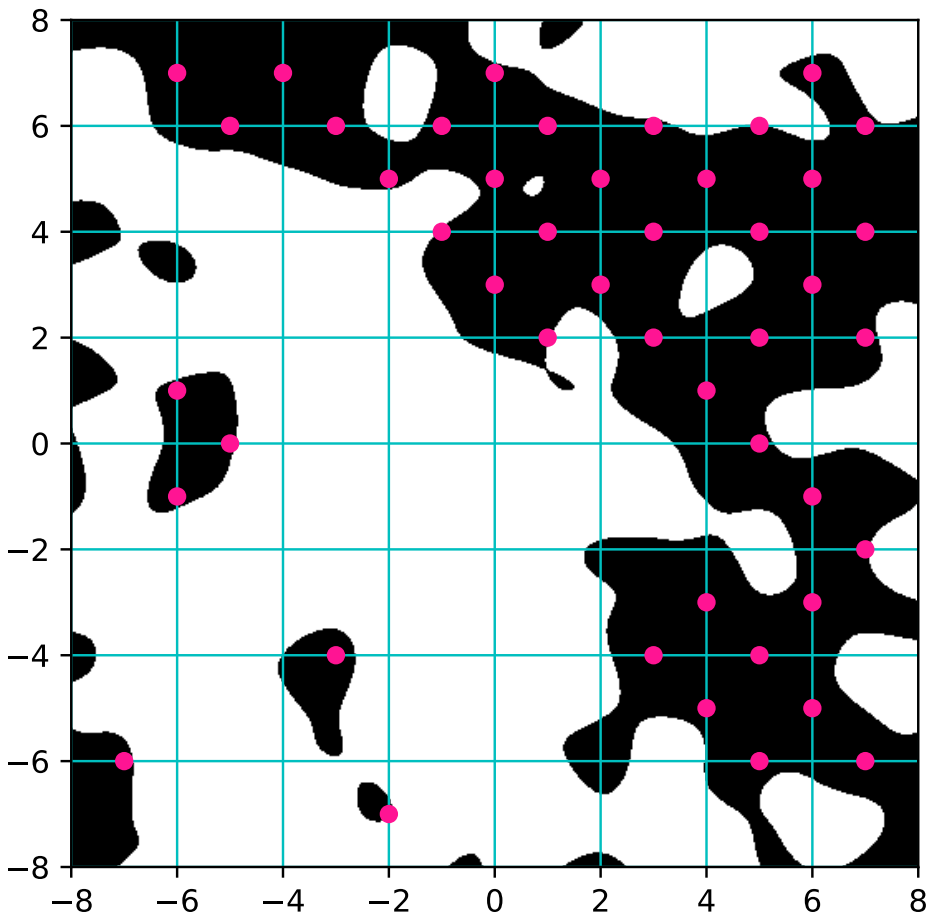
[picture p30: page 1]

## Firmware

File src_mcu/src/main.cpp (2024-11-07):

/**
 * @file    Main.cpp
 * @author  Dennis van Gils (vangils.dennis@gmail.com)
 * @version https://github.com/Dennis-van-Gils/project-TWT-jetting-grid
 * @date    07-11-2024
 *
 * @brief   Firmware for the main microcontroller of the TWT Jetting Grid. See
 * `constants.h` for a detailed description.
 *
 * This firmware is written with safety in mind:
 * 1) Out-of-bounds array operations are caught gracefully by displaying 'HALT'
 *    on the LED matrix and printing an error to the Serial console. The jetting
 *    pump will be disabled.
 * 2) When no solenoid valves are open the jetting pump will be disabled.
 * 3) Only when the MCU is running okay and at least a single solenoid valve is
 *    open, will safety pulses be send to the safety MCU, enabling the jetting
 *    pump.
 *
 * @copyright MIT License. See the LICENSE file for details.
 */

#include "CentipedeManager.h"
#include "ProtocolManager.h"
#include "constants.h"
#include "protocol_presets.h"
#include "translations.h"

#include "Adafruit_SleepyDog.h"
#include "DvG_StreamCommand.h"
#include "FastLED.h"
#include "FiniteStateMachine.h"
#include "MIKROE_4_20mA_RT_Click.h"
#include "MemoryFree.h"
#include "halt.h"

#include <Arduino.h>
#include <SPI.h>
#include <Wire.h>
#include <array>

// Serial port listener for receiving ASCII commands
const uint8_t CMD_BUF_LEN = 64;  // Length of the ASCII command buffer
char cmd_buf[CMD_BUF_LEN]{'\0'}; // The ASCII command buffer
char *str_cmd;                   // Incoming serial ASCII-command string
DvG_StreamCommand sc(Serial, cmd_buf, CMD_BUF_LEN);

// Serial port listener for receiving binary data decoding a protocol program
const uint8_t BIN_BUF_LEN = 229;          // Length of the binary data buffer
uint8_t bin_buf[BIN_BUF_LEN];             // The binary data buffer
const uint8_t EOL[] = {0xff, 0xff, 0xff}; // End-of-line sentinel
DvG_BinaryStreamCommand bsc(Serial, bin_buf, BIN_BUF_LEN, EOL, sizeof(EOL));

// Will be used externally
const uint8_t BUF_LEN = 128; // Common character buffer for string formatting
char buf[BUF_LEN]{'\0'};     // Common character buffer for string formatting

// This flag controls whether safety pulses should be send out to the safety
// microcontroller, which in turn will engage the safety relay that enables the
// jetting pump. This flag is autonomously set to `false` when none of the
// valves are currently open. If any valve is open the flag is set to `true`.
// This safety procedure can be overriden by flag `override_pump_safety`.
bool safety__allow_jetting_pump_to_run = false;

// WARNING: Safety override to always allow the jetting pump to run.
bool override_pump_safety = false;

// Debugging flags
uint32_t utick = micros();         // DEBUG timer
const bool DEBUG = false;          // Print debug info over serial?
const bool NO_PERIPHERALS = false; // Allows developing code on a bare Arduino
                                   // without sensors & actuators attached

/*------------------------------------------------------------------------------
  Readings
------------------------------------------------------------------------------*/

struct Readings {
  // Exponential moving averages (EMA) of the R Click boards
  uint32_t DAQ_obtained_DT; // Obtained oversampling interval [µs]
  float EMA_1;              // Exponential moving average of R Click 1 [bitval]
  float EMA_2;              // Exponential moving average of R Click 2 [bitval]
  float EMA_3;              // Exponential moving average of R Click 3 [bitval]
  float EMA_4;              // Exponential moving average of R Click 4 [bitval]

  // OMEGA pressure sensors
  float pres_1_mA = NAN;    // OMEGA pressure sensor 1 [mA]
  float pres_2_mA = NAN;    // OMEGA pressure sensor 2 [mA]
  float pres_3_mA = NAN;    // OMEGA pressure sensor 3 [mA]
  float pres_4_mA = NAN;    // OMEGA pressure sensor 4 [mA]
  float pres_1_bar = NAN;   // OMEGA pressure sensor 1 [bar]
  float pres_2_bar = NAN;   // OMEGA pressure sensor 2 [bar]
  float pres_3_bar = NAN;   // OMEGA pressure sensor 3 [bar]
  float pres_4_bar = NAN;   // OMEGA pressure sensor 4 [bar]
  float pres_avg_bar = NAN; // Average pressure        [bar]
};
Readings readings; // Structure holding the sensor readings and actuator states

/*------------------------------------------------------------------------------
  Macetech Centipede boards
------------------------------------------------------------------------------*/

// One object controls both Centipede boards over ports 0 to 7
CentipedeManager cp_mgr;

/*------------------------------------------------------------------------------
  LEDs
------------------------------------------------------------------------------*/

uint8_t alive_blinker_hue = HUE_GREEN;
CRGB onboard_led[1]; // Onboard NeoPixel of the Adafruit Feather M4 board
CRGB leds[N_LEDS];   // LED matrix, 16x16 RGB NeoPixel (Adafruit #2547)
uint16_t idx_led;    // Frequently used LED index

/*------------------------------------------------------------------------------
  ProtocolManager
------------------------------------------------------------------------------*/

ProtocolManager protocol_mgr(&cp_mgr);

/**
 * @brief Return the current protocol position starting at index 1.
 */
uint16_t get_protocol_position() {
  // The protocol manager internally stores the position starting at index 0
  return protocol_mgr.get_position() + 1;
}

/*------------------------------------------------------------------------------
  MIKROE 4-20 mA R Click boards for reading out the OMEGA pressure sensors
------------------------------------------------------------------------------*/

R_Click R_click_1(PIN_R_CLICK_1, R_CLICK_1_CALIB);
R_Click R_click_2(PIN_R_CLICK_2, R_CLICK_2_CALIB);
R_Click R_click_3(PIN_R_CLICK_3, R_CLICK_3_CALIB);
R_Click R_click_4(PIN_R_CLICK_4, R_CLICK_4_CALIB);

/**
 * @brief Perform an exponential moving average (EMA) on each R Click reading by
 * using oversampling and subsequent low-pass filtering.
 *
 * This function should be repeatedly called in the main loop, ideally at a
 * faster pace than the given oversampling interval `DAQ_DT` as set in
 * `constants.h`.
 *
 * @return True when a new sample has been read and added to the moving
 * average. False otherwise, because it was not yet time to read out a new
 * sample.
 */
bool R_click_poll_EMA_collectively() {
  static bool at_startup = true;
  static uint32_t tick = micros();
  uint32_t now_us = micros();
  float alpha; // Derived smoothing factor of the exponential moving average

  if ((now_us - tick) >= DAQ_DT) {
    // Enough time has passed -> Acquire a new reading.
    // Calculate the smoothing factor every time because an exact time interval
    // is not garantueed.
    readings.DAQ_obtained_DT = now_us - tick;
    alpha = 1.f - exp(-float(readings.DAQ_obtained_DT) * DAQ_LP * 1e-6);

    if (at_startup) {
      at_startup = false;
      readings.EMA_1 = R_click_1.read_bitval();
      readings.EMA_2 = R_click_2.read_bitval();
      readings.EMA_3 = R_click_3.read_bitval();
      readings.EMA_4 = R_click_4.read_bitval();
    } else {
      // Block takes 94 µs @ 1 MHz SPI clock
      // utick = micros();
      readings.EMA_1 += alpha * (R_click_1.read_bitval() - readings.EMA_1);
      readings.EMA_2 += alpha * (R_click_2.read_bitval() - readings.EMA_2);
      readings.EMA_3 += alpha * (R_click_3.read_bitval() - readings.EMA_3);
      readings.EMA_4 += alpha * (R_click_4.read_bitval() - readings.EMA_4);
      // Serial.println(micros() - utick);
    }
    tick = now_us;
    return true;

  } else {
    return false;
  }
}

/*------------------------------------------------------------------------------
  set_LED_matrix_data_fixed_grid
------------------------------------------------------------------------------*/

/**
 * @brief Set the LED colors at PCS points without a valve
 */
void set_LED_matrix_data_fixed_grid() {
  for (int8_t x = PCS_X_MIN; x <= PCS_X_MAX; x++) {
    for (int8_t y = PCS_Y_MIN; y <= PCS_Y_MAX; y++) {
      if ((x + y) % 2 == 0) { leds[p2led(P{x, y})] = CRGB(12, 12, 12); }
    }
  }
  leds[p2led(P{0, 0})] = CRGB(0, 64, 0); // Center (0, 0)
}

/*------------------------------------------------------------------------------
  Finite state machine (FSM)
------------------------------------------------------------------------------*/

uint32_t now;      // Timestamp [ms]
uint8_t idx_valve; // Frequently used valve index

// Switches the ASCII-command listener momentarily off to allow for loading in a
// new protocol program via a binary-command listener.
bool loading_program = false;

/*------------------------------------------------------------------------------
  FSM: Off

  Close all valves and idle
------------------------------------------------------------------------------*/

void FSM_fun_off__ent() {
  alive_blinker_hue = HUE_YELLOW;

  if (!NO_PERIPHERALS) {
    cp_mgr.clear_masks();
    cp_mgr.send_masks();
  }

  for (idx_valve = 0; idx_valve < N_VALVES; ++idx_valve) {
    leds[p2led(valve2p(idx_valve + 1))] = 0;
  }
}

void FSM_fun_off__upd() {}

State state_off("Off", FSM_fun_off__ent, FSM_fun_off__upd);
FiniteStateMachine fsm(state_off);

/*------------------------------------------------------------------------------
  FSM: Paused

  Leave previously activated valves open and idle
------------------------------------------------------------------------------*/

void FSM_fun_paused__ent() { alive_blinker_hue = HUE_YELLOW; }
void FSM_fun_paused__upd() {}
State state_paused("Paused", FSM_fun_paused__ent, FSM_fun_paused__upd);

/*------------------------------------------------------------------------------
  FSM: Running

  Run the jetting protocol program, advancing line for line when it is time.
  Will activate solenoid valves and will drive the LED matrix.
------------------------------------------------------------------------------*/

void FSM_fun_running__ent() { alive_blinker_hue = HUE_GREEN; }
void FSM_fun_running__upd() { protocol_mgr.update(); }
State state_running("Running", FSM_fun_running__ent, FSM_fun_running__upd);

/*------------------------------------------------------------------------------
  FSM: Uploading

  Upload a new jetting protocol program from the PC into Arduino memory
------------------------------------------------------------------------------*/

// Stage 0: Load in via ASCII the name of the protocol program.
// Stage 1: Load in via ASCII the total number of protocol lines that follow.
// Stage 2: Load in via binary the protocol program line-by-line until the
//          end-of-program (EOP) sentinel is received. The EOP is signalled by
//          receiving two end-of-line (EOL) sentinels directly after each other.
uint8_t loading_stage = 0;
bool loading_successful = false;

void FSM_fun_uploading__ent() {
  alive_blinker_hue = HUE_BLUE;
  loading_program = true;
  loading_stage = 0;
  loading_successful = false;
  protocol_mgr.clear();
}
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

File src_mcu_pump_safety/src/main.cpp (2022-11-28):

/**
 * @file    Main.cpp
 * @author  Dennis van Gils (vangils.dennis@gmail.com)
 * @version https://github.com/Dennis-van-Gils/project-TWT-jetting-grid
 * @date    28-11-2022
 *
 * @brief   Firmware for the pump safety microcontroller.
 *
 * @copyright MIT License. See the LICENSE file for details.
 */

/*------------------------------------------------------------------------------
  PURPOSE
--------------------------------------------------------------------------------

There are two microcontroller (MCU) boards used in the TWT jetting grid. The
main MCU (Adafruit M4 Feather Express) is responsible for driving the solenoid
valves and LED matrix and communicates via USB to the Python main program
running on a PC. The second MCU (Adafruit Feather M0 Basic Proto) acts as a
safety controller, governing the relay that allows turning the jetting pump on
and off via terminal X1 of its frequency inverter.

The main MCU should send a digital 'safety' pulse at least once every
`SAFETY_PULSE_TIMEOUT` ms over to the safety MCU as indication that the main MCU
is still operating all right. As long as the safety MCU receives pulses within
the set time period, the 'pump on' relay will be engaged.
*/

#include "Adafruit_SleepyDog.h"
#include <Arduino.h>

const uint8_t PIN_PUMP_RELAY = 5;
const uint8_t PIN_PUMP_FRONT_PANEL_LED = 10;
const uint8_t PIN_SAFETY_PULSE_IN = A0;
const uint16_t SAFETY_PULSE_TIMEOUT = 100; // [ms]

// The microcontroller will auto-reboot when it fails to get a
// `Watchdog.reset()` within this time period [ms]
const uint16_t WATCHDOG_TIMEOUT = 200; // [ms]

volatile bool received_pulse = false;
void my_isr() { received_pulse = true; }

/*------------------------------------------------------------------------------
  setup
------------------------------------------------------------------------------*/

void setup() {
  // Pump relay
  pinMode(PIN_PUMP_RELAY, OUTPUT);
  digitalWrite(PIN_PUMP_RELAY, LOW);

  // Front panel LED indicating pump relay status
  pinMode(PIN_PUMP_FRONT_PANEL_LED, OUTPUT);
  digitalWrite(PIN_PUMP_FRONT_PANEL_LED, LOW);

  // Onboard LED always on
  pinMode(PIN_LED, OUTPUT);
  digitalWrite(PIN_LED, HIGH);

  // Safety pulses coming from the main MCU
  pinMode(PIN_SAFETY_PULSE_IN, INPUT_PULLDOWN);
  attachInterrupt(digitalPinToInterrupt(PIN_SAFETY_PULSE_IN), my_isr, RISING);

  Watchdog.enable(WATCHDOG_TIMEOUT);
}

/*------------------------------------------------------------------------------
  loop
------------------------------------------------------------------------------*/

void loop() {
  uint32_t now = millis();
  static uint32_t tick_watchdog = now;
  static uint32_t tick_safety_pulse = now;
  static bool engage_relay = false;
  static bool prev_state_relay = false;

  noInterrupts();
  if (received_pulse) {
    received_pulse = false;
    tick_safety_pulse = now;
    engage_relay = true;
  }
  interrupts();

  if (now - tick_safety_pulse > SAFETY_PULSE_TIMEOUT) {
    engage_relay = false;
  }

  if (prev_state_relay != engage_relay) {
    digitalWrite(PIN_PUMP_RELAY, engage_relay);
    digitalWrite(PIN_PUMP_FRONT_PANEL_LED, engage_relay);
    prev_state_relay = engage_relay;
  }

  if (now - tick_watchdog > 1) { // Slowed down, because of overhead otherwise
    Watchdog.reset();
    tick_watchdog = now;
  }
}

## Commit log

2022-07-14 Renumber pressure CS 'cable select' wires
2022-07-19 Added LED matrix connectors
    [shopping_list.xlsx]
2022-07-19 Embedded oversample & LP filter into class `R_Click()`
2022-07-21 Turned `DvG_RT_Click_mA` library into a separate Arduino lib.
2022-07-26 Brainstorming: valve to matrix transformation
    [jetting_grid_indices.xlsx]
2022-07-27 Finished indices
    [jetting_grid_indices.xlsx]
2022-07-28 Stable timings on all subsystems
    Including:
    - 16x16 LED matrix @ 50 fps
    - R Clicks @ 100 Hz polling rate
    - Centipedes @ 1 MHz clock rate
2022-07-28 Update jetting_grid_indices.xlsx
    Added text to import as matrix inside CPP source code
    [jetting_grid_indices.xlsx]
2022-07-29 Hackaton: reverse look-up `valve2PCS`
2022-08-03 Comment: Refer to `ARR__PCS2VALVE` for the valve numbering layout
2022-08-10 Compiler error: multiple definition of `VALVE2P'
2022-08-16 Finalized the framework of class `ProtocolManager`
2022-08-17 Color LEDs of non-valves yellow. Improved LEDs painting.
2022-08-19 LED matrix
    [Adafruit_2547_flexible_16x16_NeoPixel_LED_matrix.SLDPRT, LED_matrix_backing_plate.DXF, LED_matrix_backing_plate.SLDASM, LED_matrix_backing_plate.SLDPRT]
2022-08-22 Cable sleeve
    [cable_sleeve_3D_print.SLDPRT, cable_sleeve_3D_print.STL]
2022-08-22 Working minimal FSM framework
2022-08-23 Working proof of concept: Python <-> Arduino protocol
2022-08-25 Also show red on onboard LED
2022-08-30 Prefix '_' to private class members, not postfix. Added pretty prints.
2022-08-31 Clear all valve leds at program start.
2022-09-05 Bump SW2022
    [1424137.SLDPRT, 3273334.SLDASM, 3273344.SLDASM, 3274056.SLDPRT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]
2022-09-05 Hinge door the other way
    [1076_000_1__10.sldprt, 1076_000_1__12.sldprt, 1076_000_1__25_customized.SLDPRT, 1076_000_1__27.sldprt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]
2022-10-18 Line buffer set to open all valves when protocol is cleared
2022-10-21 Fake pressure data when DEVELOPER_MODE_WITHOUT_PERIPHERALS==1
2022-10-21 Initial framework ready
2022-10-26 More shopping
    [shopping_list.xlsx]
2022-10-31 New jetting grid indices
    [jetting_grid_indices.xlsx]
2022-11-17 Alternative demo: Single valve run
2022-11-17 Added DB9 connectors
    [1076_000_1__25_customized.SLDDRW, 1076_000_1__25_customized.SLDPRT, 1076_000_1_customized.SLDASM]
2022-11-21 Pump safety MCU
2022-11-28 Added "pump enabled" LED indicator
2022-11-28 Working framework 'safety pulses'
2022-11-28 Implemented jetting pump safety
2022-11-29 Added resistor to A0 to prevent phantom powering safety MCU
2022-12-02 Added front panel LED "PUMP ENABLED"
2022-12-02 Ditch `transfer_next_line_to_buffer()` method. Instead, we work with the current line.
2022-12-02 Implicitly print to Serial. Not longer a passed argument.
2023-01-27 Adding in valve locations
2023-02-01 Added `valve2pcs` transformations
2023-02-01 Reduce figure size. Demo plot `valve 0` timeseries
2023-02-02 Plot valves and noise transparency
2023-02-03 Refactor: Move valve transformations to `constants.py`
2023-02-03 Removed figure 3 on valve timeseries
2023-02-07 Set dtype `valves_stack` to int8
2023-02-07 New protocol with adjusted valve times
2023-02-08 Comment on max frames
2023-02-08 Streamlining code. Exporting `valves_stack.npy`
2023-02-08 PDFs of `valve on/off` durations are in units of seconds now
2023-02-08 Streamlined exporting data to disk. Using new `valve_on_off_PDFs()` function
2023-02-14 Ready for print-out
    [jetting_grid_indices.xlsx]
2023-02-14 Ready for designing casing
    [Adafruit_2547_flexible_16x16_NeoPixel_LED_matrix.SLDPRT, LED_matrix_backing_plate.SLDASM, LED_matrix_backing_plate.SLDPRT, LED_matrix_diffusor.SLDPRT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]
2023-02-15 Disabled printing current protocol line to serial
2023-02-15 Framework in progress
2023-02-17 Framework nearly done
2023-02-23 Ready for integration into `dvg-devices`
2023-02-23 `query_bytes()` got integrated into `dvg-devices.BaseDevice`
2023-03-02 Work in progress: GUI
    [gui.xlsx]
2023-03-02 Added reading nominal motor current
    NOTE: Strange byte sizes used by HVL firmware. Not in line with ModBus specification.
2023-03-03 Fixed reading nominal motor current
2023-03-03 Test: Pump enabled/disabled/on/off
2023-03-22 In progress: merging GUIs `jetting pump` and `Arduino`
2023-03-22 Color coding LED panel
2023-03-23 Added cable colors
2023-03-23 Rotated LED matrix by 90 deg CW
    [jetting_grid_indices.xlsx]
2023-03-23 Lower LP filter on pressures
2023-03-23 Plot pump pressures
2023-03-24 Slow down jetting pump DAQ rate
2023-03-30 Implemented: `pump reached standstill` detection, GUI controls for protocol ON/OFF/PAUSE
2023-03-30 Note on minimum valve duration
2023-03-30 First column is duration in milliseconds, not timestamp
2023-03-30 Refactor: renamed variable `hvl` to `pump`
2023-03-30 Closing `pump` at exit
2023-03-31 Docstr & add access to low-level devices
2023-03-31 Preset "single valve" duration set to 500 ms
2023-03-31 Changed Arduino ID to "Jetting Grid"
2023-03-31 Print FSM name to serial
2023-04-11 Finalizing serial commands
    Protocol position is reported with index starting at 1, instead of at 0
    [Serial_commands.xlsx]
2023-04-12 Now reporting protocol position. Added presets.
    [Serial_commands.xlsx]
2023-04-12 In progress: rewrite low-level Arduino control
2023-04-12 Major change: Added `JettingGrid_Arduino` class
    Better flow of program control. Member `state` has been moved from `JettingGrid_qdev` to JettingGrid_Arduino` instead.
2023-04-13 Implemented play/stop/pause/rewind/step controls
    [Serial_commands.xlsx]
2023-04-13 Renumbered protocol presets
    [Serial_commands.xlsx]
2023-04-14 Major changes: streamlined presets mechanism & keeping track of protocol name
    [Serial_commands.xlsx]
2023-04-14 Set up quick and dirty framework for file navigation
2023-04-18 Updated valve transparency
2024-09-11 Round we go
    [image_stack.SLDPRT]
2024-09-16 Print stats to terminal
2024-09-20 New figures for publication & restructured folder
    [4D_noise_loop.SLDPRT, image_stack.SLDPRT]
2024-11-07 Added pressure VU meter to the LED panel
